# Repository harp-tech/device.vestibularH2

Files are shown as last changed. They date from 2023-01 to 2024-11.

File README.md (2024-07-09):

## Harp VestibularH2

This repository contains the device metadata, firmware and high-level interface to the VestibularH2 device. Below are simple getting started instructions for maintainers to create a new device using the automatic code generators.

### Device metadata

#### Prerequisites

1. Install [Visual Studio Code](https://code.visualstudio.com/)
2. Install the [YAML](https://marketplace.visualstudio.com/items?itemName=redhat.vscode-yaml) extension.

The `device.yml` file in the root of the project contains the VestibularH2 device metadata. A complete specification of device registers, including any bit masks, group masks, and payload specs needs to be provided for code generation to work.

### Generating interface and firmware

#### Prerequisites

1. Install [`dotnet`](https://dotnet.microsoft.com/)
2. Install `dotnet-t4`
```
dotnet tool install -g dotnet-t4
```

The `Generators` folder contains all text templates and project files required to generate both the firmware headers and the interface for the VestibularH2 device. To run the text templating engine just build the project inside this folder.

```
cd Generators
dotnet build
```

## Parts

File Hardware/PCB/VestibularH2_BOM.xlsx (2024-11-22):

VestibularVR H2-module v1.1
.on board
Qty | Parts | Value | OEPS | MPN | Device | Package | Description
21 | C1, C3, C5, C7, C9, C12, C14, C16, C17, C18, C25, C26, C27, C19, C20, C21, C22, C28, C29, C30, C31 | 100nF | OEPS010004 | C1005X7R1H104K050BB | C-EUC0402K | C0402K | CAPACITOR, European symbol
1 | R5 | 10R | OEPS020041 | ERJ-PA2J100X | R-US_R0402 | R0402 | RESISTOR, American symbol
12 | R2, R6, R8, R10, R11, R12, R13, R14, R17, R18, R19, R34 | 10k | OEPS020030 | CRCW040210K0FKED | R-US_R0402 | R0402 | RESISTOR, American symbol
1 | R21 | 15k | OEPS020015 | ERJ-2RKF1502X | R-EU_R0402 | R0402 | RESISTOR, European symbol
2 | C41, C42 | 15nF 5% | OEPS010023 | CGA2B3X7R1V153K050BB | C-EUC0402K | C0402K | CAPACITOR, European symbol
1 | R3 | 1M | OEPS020026 | CRCW04021M00FKED | R-US_R0402 | R0402 | RESISTOR, American symbol
1 | X3 | 1x2 case | OEPS070020 | 282834-2 | 22-23-2021 | 22-23-2021 | .100 (2.54mm) Center Header - 2 Pin"
2 | X4, X10 | 1x3 case | OEPS070035 | 282834-3 | 22-23-2031 | 22-23-2031 | .100 (2.54mm) Center Header - 3 Pin"
1 | X1 | 1x5 MAIN PLUG | OEPS070037 | 20.155MH/5-E | 90G-5 | 90G-5 | WEIDMUELLER CLAMP CONNECTOR
3 | X2, X5, X9 | 1x5 case | OEPS070041 | 282834-5 | 22-23-2051 | 22-23-2051 | .100 (2.54mm) Center Header - 5 Pin"
1 | R20 | 24k | OEPS020048 | ERJ-2RKF2402X | R-EU_R0402 | R0402 | RESISTOR, European symbol
1 | R1 | 330R | OEPS020037 | RC0402FR-07330RL | R-US_R0402 | R0402 | RESISTOR, American symbol
1 | C2 | 4.7nF | OEPS010001 | CC0402KRX7R8BB472 | C-EUC0402K | C0402K | CAPACITOR, European symbol
5 | C8, C10, C11, C23, C24 | 4.7uF | OEPS010018 | C1608X6S1C475K080AC | C-EUC0603K | C0603K | CAPACITOR, European symbol
3 | L1, L2, L3 | 40R@100MHz | OEPS040003 | MI0805K400R-10 | R-EU_R0805 | R0805 | RESISTOR, European symbol
3 | C4, C6, C13 | 47pF | OEPS010011 | 04025A470JAT2A | C-EUC0402K | C0402K | CAPACITOR, European symbol
1 | IC8 | ATXMEGA32A4U | OEPS080012 | ATXMEGA32A4U-AUR | XMEGA-A4_AT-XMEGA-XXA4-AUTQFP44 | TQFP44 | ATxMega a4 Serie
1 | X8 | CLCK_JACK | OEPS070025 | 35RASMT2BHNTRX | STEREO_JACK | 35RASMT2BHNTRX | CONN JACK STEREO 3.5MM SMD R/A
1 | X7 | DC_JACK2.1MM | OEPS070026 | 163-179PH-EX | DC_JACK2.1MM | DC_POWER_INPUT_2.1MM | DC Power Connectors PCB 2.1MM
1 | C15 | DNI | DNI | DNI | C-EUC0603K | C0603K | CAPACITOR, European symbol
3 | R4, R7, R9 | DNI | DNI | DNI | R-US_R0402 | R0402 | RESISTOR, American symbol
1 | IC1 | FT232RL | OEPS080013 | FT232RL | FT232RL | SSOP28 | UART/FIFO IC
1 | STATE | GREEN_LED | OEPS030005 | LTST-C191KGKT | LEDCHIP-LED0603 | CHIP-LED0603
2 | IC3, IC9 | LP5907MFX-3.3 | OEPS080016 | LP5907MFX-3.3/NOPB | TLV700XX | TSOT23-5 | C REG LINEAR 3.3V 200MA SOT23-5
12 | IC2, IC4, IC5, IC6, IC11, IC12, IC13, IC14, IC15, C16, IC17, IC18 | M74VHC1GT126DT1G | OEPS080017 | M74VHC1GT126DT1G | M74VHC1GT126DT1G | TSOP-5
1 | OSC1 | OSCILLATOR | OEPS080018 | DSC1001CI5-032.0000 | OSCILLATOR | OSCILLATOR_3.2X2.5 | XTAL OSC TCXO 32.0000MHZ HCMOS
1 | SV2 | PINHD-2X3 | OEPS070015 | 609-3210-ND | PINHD-2X3 | 2X03 | PIN HEADER
1 | IC10 | THS4281DBVT | OEPS080038 | THS4281DBVT | OPA365 | SOT23-5
1 | IC7 | USBLC6-2SC6 | OEPS030010 | USBLC6-2SC6 | USBLC6-2SC6 | SOT23-6L | TVS DIODE 5.25VWM 17VC SOT23-6
1 | X6 | USB_MINI_B | OEPS070021 | UX60-MB-5S8 | USB_MINI_B | 240-0002-1 | CONN RCPT USB2.0 MINI B SMD R/A
.off board
N.A.

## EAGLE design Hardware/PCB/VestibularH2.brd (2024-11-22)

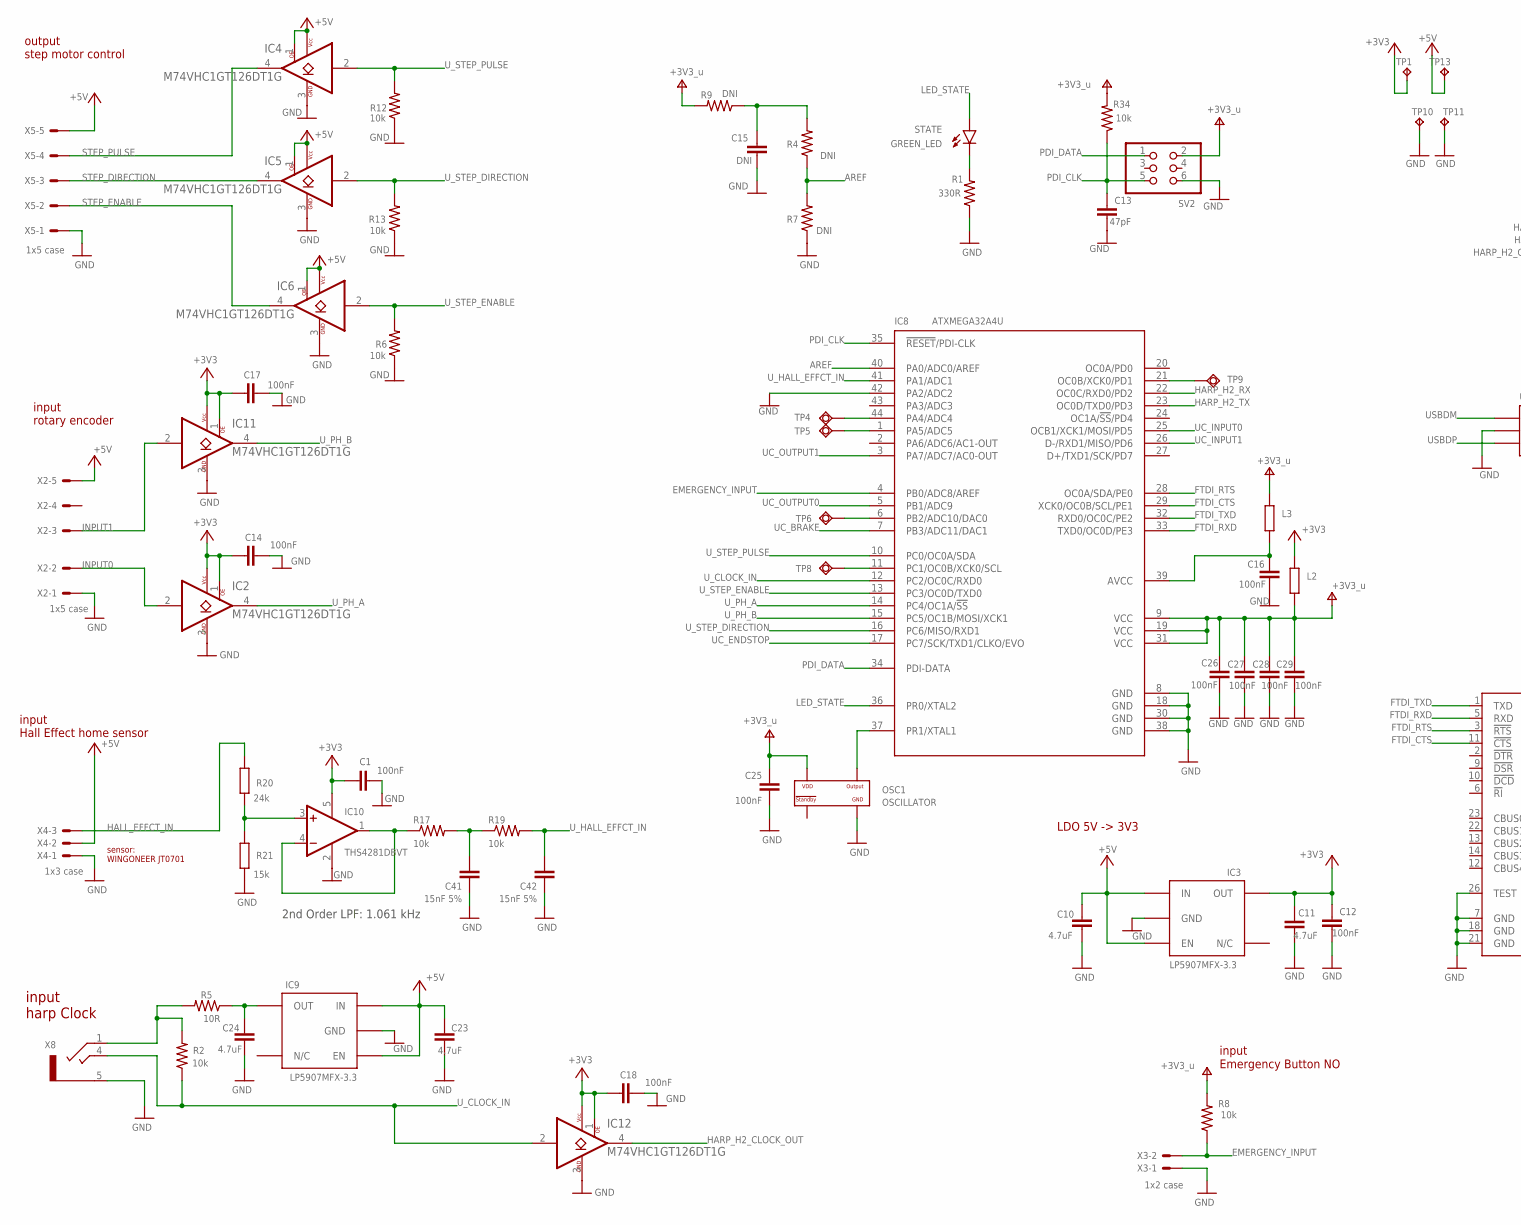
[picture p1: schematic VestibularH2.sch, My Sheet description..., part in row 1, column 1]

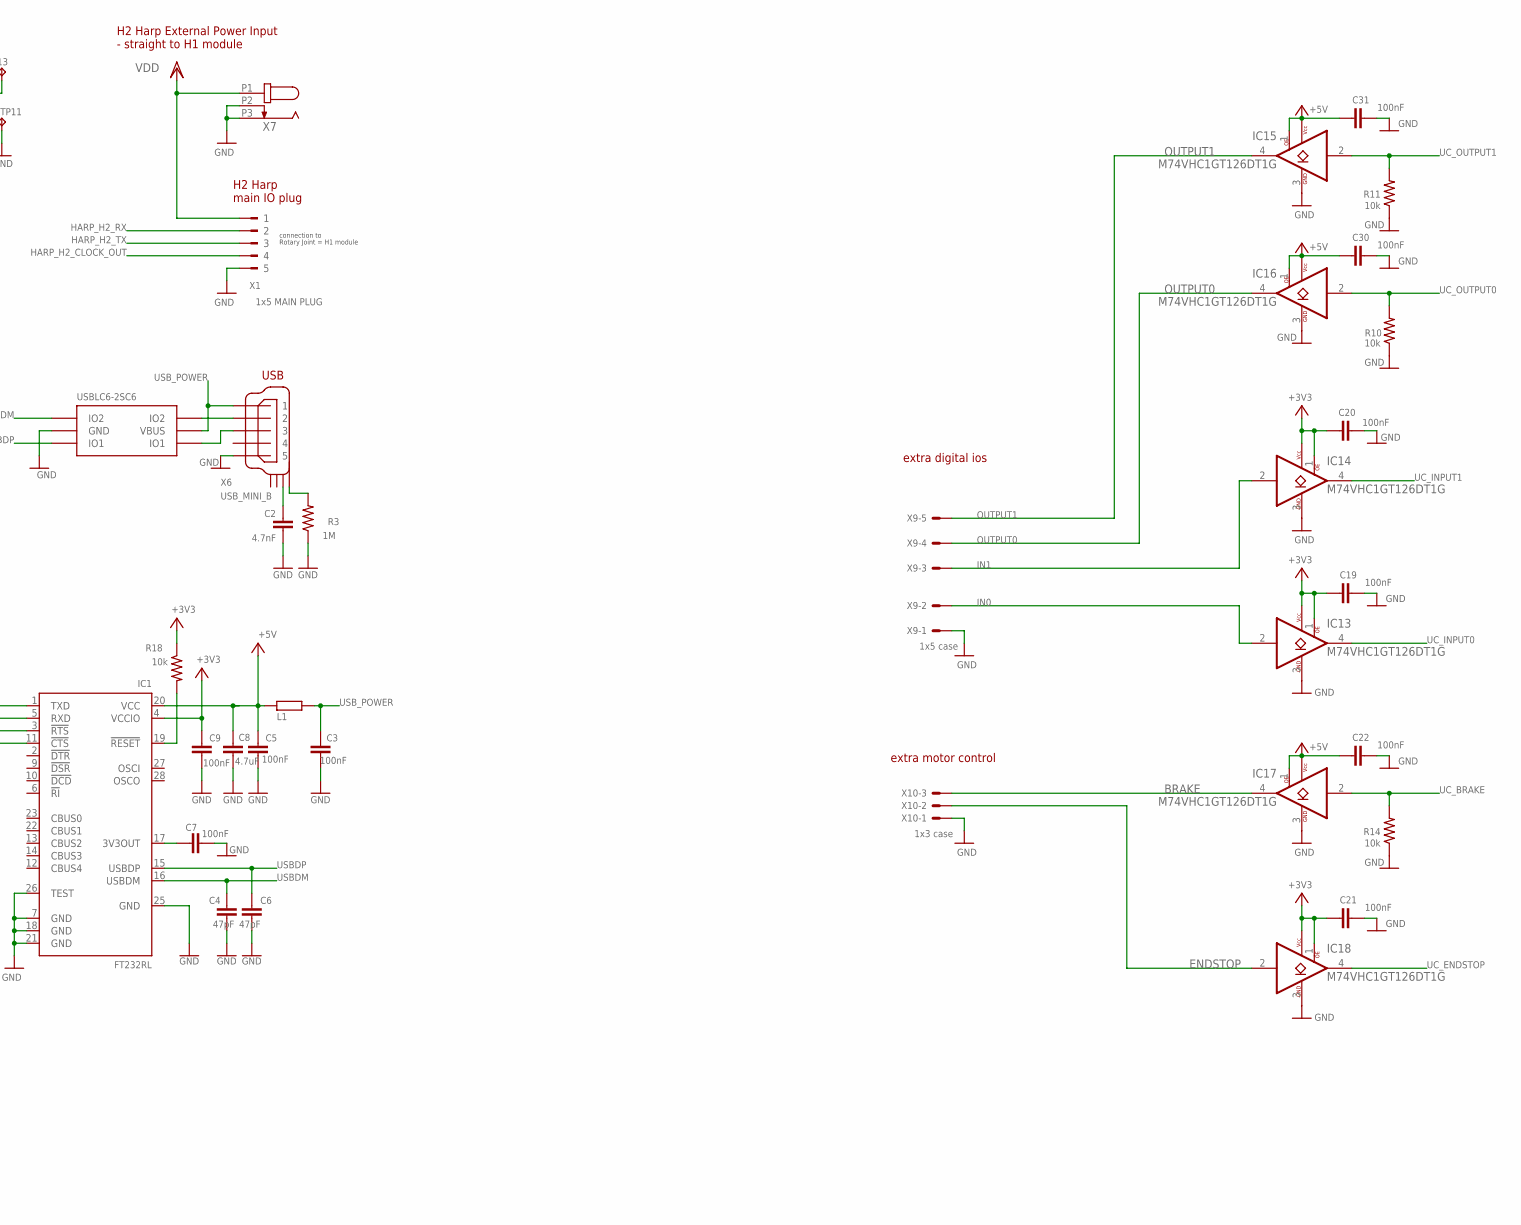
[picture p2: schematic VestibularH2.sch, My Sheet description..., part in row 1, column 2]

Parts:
C1, C3, C5, C7, C9, C12, C14, C16, C17, C18, C19, C20, C21, C22, C25, C26, C27, C28, C29, C30, C31: 100nF; C0402K; MPN C1005X7R1H104K050BB
C2: 4.7nF; C0402K; MPN CC0402KRX7R8BB472
C4, C6, C13: 47pF; C0402K; MPN 04025A470JAT2A
C8, C10, C11, C23, C24: 4.7uF; C0603K; MPN C1608X6S1C475K080AC
C15: DNI; C0603K; MPN DNI
C41, C42: 15nF 5%; C0402K; MPN CGA2B3X7R1V153K050BB
IC1: FT232RL; SSOP28; MPN FT232RL
IC2, IC4, IC5, IC6, IC11, IC12, IC13, IC14, IC15, IC16, IC17, IC18: M74VHC1GT126DT1G; TSOP-5; MPN M74VHC1GT126DT1G; DIGIKEY_PN M74VHC1GT126DT1GOSDKR-ND
IC3, IC9: LP5907MFX-3.3; TSOT23-5; MPN LP5907MFX-3.3/NOPB
IC7: USBLC6-2SC6; SOT23-6L; MPN USBLC6-2SC6
IC8: ATXMEGA32A4U; TQFP44; MPN ATXMEGA32A4U-AUR
IC10: THS4281DBVT; SOT23-5; MPN THS4281DBVT
L1, L2, L3: 40R@100MHz; R0805; MPN MI0805K400R-10
OSC1: OSCILLATOR; OSCILLATOR_3.2X2.5; MPN DSC1001CI5-032.0000
R1: 330R; R0402; MPN RC0402FR-07330RL
R2, R6, R8, R10, R11, R12, R13, R14, R17, R18, R19, R34: 10k; R0402; MPN CRCW040210K0FKED
R3: 1M; R0402; MPN CRCW04021M00FKED
R4, R7, R9: DNI; R0402; MPN DNI
R5: 10R; R0402; MPN ERJ-PA2J100X
R20: 24k; R0402; MPN ERJ-2RKF2402X
R21: 15k; R0402; MPN ERJ-2RKF1502X
STATE: GREEN_LED; CHIP-LED0603; MPN LTST-C191KGKT
SV2: PINHD-2X3; 2X03; MPN 609-3210-ND
TP1, TP10, TP11, TP13: NO_COMPONENT; B1,27
TP4, TP5, TP6, TP8, TP9: NO_COMPONENT; TP11R
X1: 1x5 MAIN PLUG; 90G-5; MPN 20.155MH/5-E
X2, X5, X9: 1x5 case; 22-23-2051; MPN 282834-5
X3: 1x2 case; 22-23-2021; MPN 282834-2
X4, X10: 1x3 case; 22-23-2031; MPN 282834-3
X6: USB_MINI_B; 240-0002-1; MPN UX60-MB-5S8
X7: DC_JACK2.1MM; DC_POWER_INPUT_2.1MM; MPN 163-179PH-EX
X8: CLCK_JACK; 35RASMT2BHNTRX; MPN 35RASMT2BHNTRX

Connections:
+3V3: C1.1, C9.1, C11.1, C12.1, C14.1, C17.1, C18.1, C19.1, C20.1, C21.1, IC1.4 (VCCIO), IC2.1 (OE), IC2.5 (VCC), IC3.5 (OUT), IC10.5 (V+), IC11.1 (OE), IC11.5 (VCC), IC12.1 (OE), IC12.5 (VCC), IC13.1 (OE), IC13.5 (VCC), IC14.1 (OE), IC14.5 (VCC), IC18.1 (OE), IC18.5 (VCC), L2.2, R18.1, TP1.TP
+5V: C5.1, C8.1, C10.1, C22.1, C23.1, C30.1, C31.1, IC1.20 (VCC), IC3.1 (IN), IC3.3 (EN), IC4.1 (OE), IC4.5 (VCC), IC5.1 (OE), IC5.5 (VCC), IC6.1 (OE), IC6.5 (VCC), IC9.1 (IN), IC9.3 (EN), IC15.1 (OE), IC15.5 (VCC), IC16.1 (OE), IC16.5 (VCC), IC17.1 (OE), IC17.5 (VCC), L1.1, TP13.TP, X2.5, X4.2, X5.5
AREF: IC8.40 (PA0/ADC0/AREF), R4.1, R7.2
BRAKE: IC17.4 (Y), X10.3
EMERGENCY_INPUT: IC8.4 (PB0/ADC8/AREF), R8.1, X3.2
ENDSTOP: IC18.2 (A), X10.2
FTDI_CTS: IC1.11 (!CTS), IC8.29 (XCK0/OC0B/SCL/PE1)
FTDI_RTS: IC1.3 (!RTS), IC8.28 (OC0A/SDA/PE0)
FTDI_RXD: IC1.5 (RXD), IC8.33 (TXD0/OC0D/PE3)
FTDI_TXD: IC1.1 (TXD), IC8.32 (RXD0/OC0C/PE2)
GND: C1.2, C2.2, C3.2, C4.2, C5.2, C6.2, C7.2, C8.2, C9.2, C10.2, C11.2, C12.2, C13.2, C14.2, C15.2, C16.2, C17.2, C18.2, C19.2, C20.2, C21.2, C22.2, C23.2, C24.2, C25.2, C26.2, C27.2, C28.2, C29.2, C30.2, C31.2, C41.1, C42.1, IC1.7 (GND), IC1.18 (GND), IC1.21 (GND), IC1.25 (GND), IC1.26 (TEST), IC2.3 (GND), IC3.2 (GND), IC4.3 (GND), IC5.3 (GND), IC6.3 (GND), IC7.P$2 (GND), IC8.8 (GND), IC8.18 (GND), IC8.30 (GND), IC8.38 (GND), IC8.42 (PA2/ADC2), IC9.2 (GND), IC10.2 (V-), IC11.3 (GND), IC12.3 (GND), IC13.3 (GND), IC14.3 (GND), IC15.3 (GND), IC16.3 (GND), IC17.3 (GND), IC18.3 (GND), OSC1.P$2 (GND), R1.1, R3.1, R6.1, R7.1, R10.1, R11.1, R12.1, R13.1, R14.1, R21.1, SV2.6, TP10.TP, TP11.TP, X1.5, X2.1, X3.1, X4.1, X5.1, X6.P$5 (5), X7.P2 (2), X7.P3 (3), X8.5, X9.1, X10.1
HALL_EFFCT_IN: R20.2, X4.3
HARP_H2_CLOCK_OUT: IC12.4 (Y), X1.4
HARP_H2_RX: IC8.22 (OC0C/RXD0/PD2), X1.2
HARP_H2_TX: IC8.23 (OC0D/TXD0/PD3), X1.3
IN0: IC13.2 (A), X9.2
IN1: IC14.2 (A), X9.3
INPUT0: IC2.2 (A), X2.2
INPUT1: IC11.2 (A), X2.3
LED_STATE: IC8.36 (PR0/XTAL2), STATE.A
unnamed: R3.2, X6.SHIELD_4
unnamed: IC7.P$4 (IO2), X6.P$2 (2)
unnamed: IC7.P$6 (IO1), X6.P$3 (3)
unnamed: R1.2, STATE.C
unnamed: IC8.44 (PA4/ADC4), TP4.TP
unnamed: IC8.1 (PA5/ADC5), TP5.TP
unnamed: IC8.6 (PB2/ADC10/DAC0), TP6.TP
unnamed: C2.1, X6.SHIELD_3
unnamed: IC8.11 (PC1/OC0B/XCK0/SCL), TP8.TP
unnamed: IC8.21 (OC0B/XCK0/PD1), TP9.TP
unnamed: C7.1, IC1.17 (3V3OUT)
unnamed: C41.2, R17.2, R19.1
unnamed: C15.1, R4.2, R9.1
unnamed: C16.1, IC8.39 (AVCC), L3.1
unnamed: IC10.1 (OUT), IC10.4 (-IN), R17.1
unnamed: IC10.3 (+IN), R20.1, R21.2
unnamed: R2.2, R5.2, X8.1
unnamed: C24.1, IC9.5 (OUT), R5.1
unnamed: IC1.19 (!RESET), R18.2
OSC2: IC8.37 (PR1/XTAL1), OSC1.P$3 (OUTPUT)
OUTPUT0: IC16.4 (Y), X9.4
OUTPUT1: IC15.4 (Y), X9.5
PDI_CLK: C13.1, IC8.35 (!RESET!/PDI-CLK), R34.1, SV2.5
PDI_DATA: IC8.34 (PDI-DATA), SV2.1
STEP_DIRECTION: IC5.4 (Y), X5.3
STEP_ENABLE: IC6.4 (Y), X5.2
STEP_PULSE: IC4.4 (Y), X5.4
UC_BRAKE: IC8.7 (PB3/ADC11/DAC1), IC17.2 (A), R14.2
UC_ENDSTOP: IC8.17 (PC7/SCK/TXD1/CLKO/EVO), IC18.4 (Y)
UC_INPUT0: IC8.25 (OCB1/XCK1/MOSI/PD5), IC13.4 (Y)
UC_INPUT1: IC8.26 (D-/RXD1/MISO/PD6), IC14.4 (Y)
UC_OUTPUT0: IC8.5 (PB1/ADC9), IC16.2 (A), R10.2
UC_OUTPUT1: IC8.3 (PA7/ADC7/AC0-OUT), IC15.2 (A), R11.2
USBDM: C4.1, IC1.16 (USBDM), IC7.P$3 (IO2)
USBDP: C6.1, IC1.15 (USBDP), IC7.P$1 (IO1)
USB_POWER: C3.1, IC7.P$5 (VBUS), L1.2, X6.P$1 (1)
U_CLOCK_IN: IC8.12 (PC2/OC0C/RXD0), IC12.2 (A), R2.1, X8.4
U_HALL_EFFCT_IN: C42.2, IC8.41 (PA1/ADC1), R19.2
U_PH_A: IC2.4 (Y), IC8.14 (PC4/OC1A/!SS)
U_PH_B: IC8.15 (PC5/OC1B/MOSI/XCK1), IC11.4 (Y)
U_STEP_DIRECTION: IC5.2 (A), IC8.16 (PC6/MISO/RXD1), R13.2
U_STEP_ENABLE: IC6.2 (A), IC8.13 (PC3/OC0D/TXD0), R6.2
U_STEP_PULSE: IC4.2 (A), IC8.10 (PC0/OC0A/SDA), R12.2
V+: C25.1, C26.1, C27.1, C28.1, C29.1, IC8.9 (VCC), IC8.19 (VCC), IC8.31 (VCC), L2.1, L3.2, OSC1.P$4 (VDD), R8.2, R9.2, R34.2, SV2.2
VDD: X1.1, X7.P1 (1)

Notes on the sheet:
H2 Harp main IO plug
input rotary encoder
input Hall Effect home sensor
input harp Clock
output step motor control
input Emergency Button NO
USB
sensor: WINGONEER JT0701
H2 Harp External Power Input - straight to H1 module
connection to Rotary Joint = H1 module
2nd Order LPF: 1.061 kHz
LDO 5V -> 3V3
extra digital ios
extra motor control

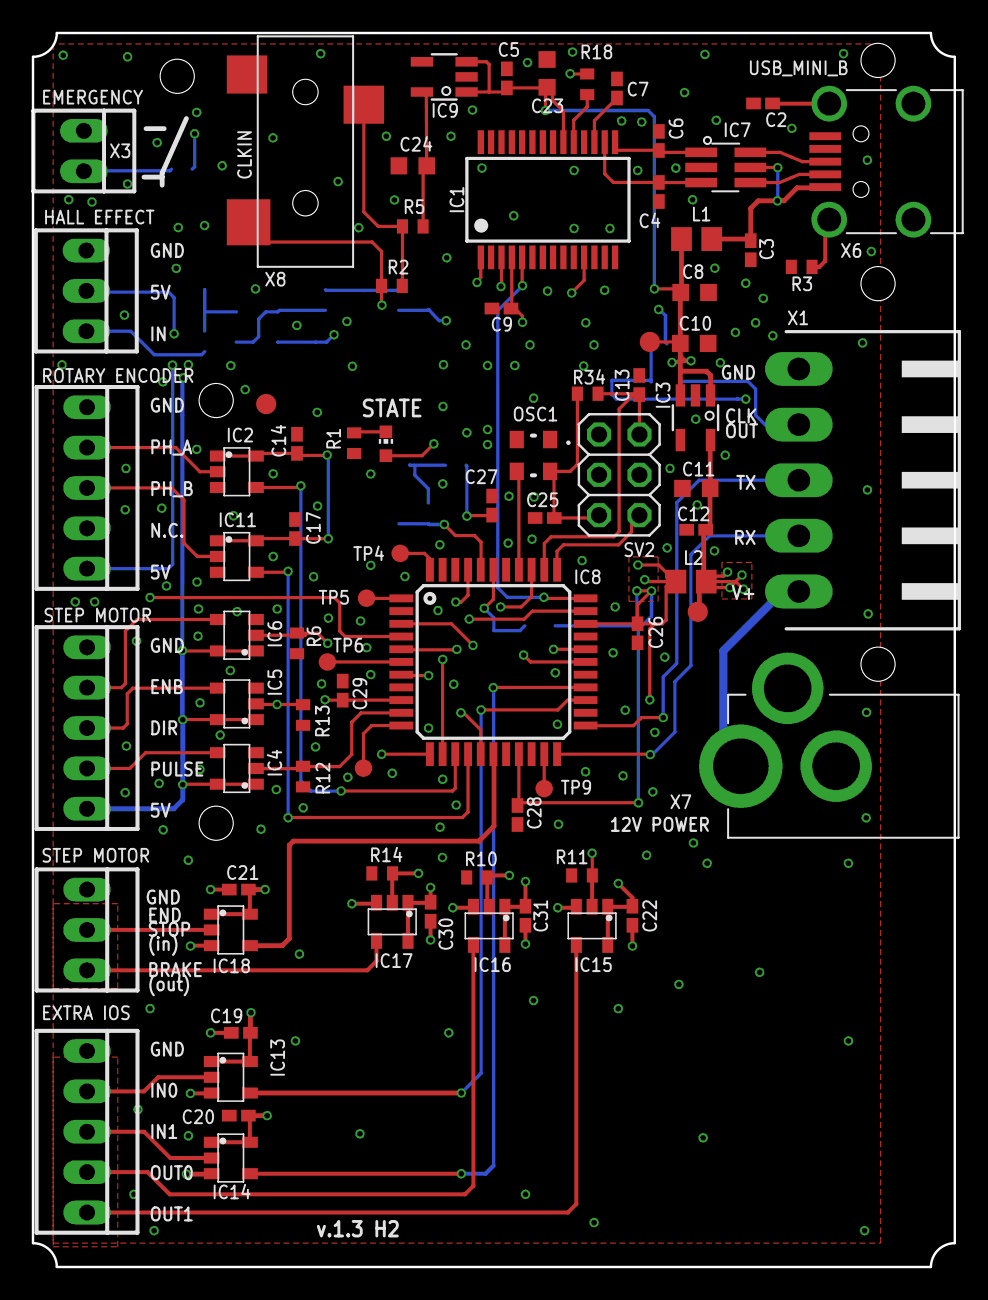
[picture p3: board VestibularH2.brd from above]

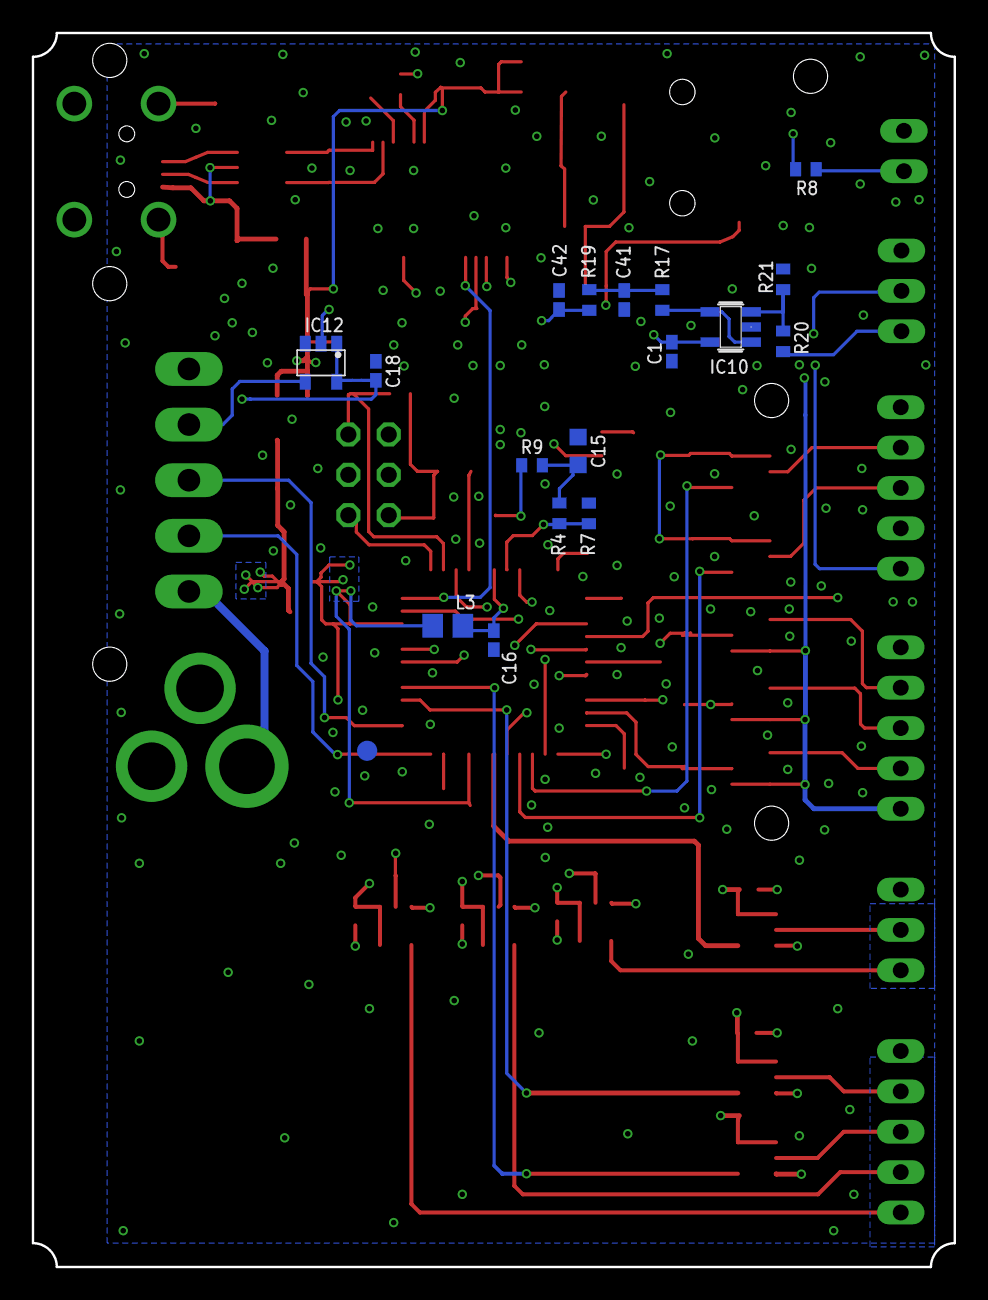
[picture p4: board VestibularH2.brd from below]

Board: 4 copper layers, 58.0 x 77.6 mm, 96 parts (18 on the bottom side), 65 nets.

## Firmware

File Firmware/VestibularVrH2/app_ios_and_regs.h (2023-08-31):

#ifndef _APP_IOS_AND_REGS_H_
#define _APP_IOS_AND_REGS_H_
#include "cpu.h"

void init_ios(void);
/************************************************************************/
/* Definition of input pins                                             */
/************************************************************************/
// STOP_SWITCH            Description: Emergency stop indication

#define read_STOP_SWITCH read_io(PORTB, 0)      // STOP_SWITCH

/************************************************************************/
/* Definition of output pins                                            */
/************************************************************************/
// MOTOR_ENABLE           Description: Enable the motor external driver
// MOTOR_PULSE            Description: Moves one step
// MOTOR_DIRECTION        Description: Sets the motor direction

/* MOTOR_ENABLE */
#define set_MOTOR_ENABLE clear_io(PORTC, 3)
#define clr_MOTOR_ENABLE set_io(PORTC, 3)
#define tgl_MOTOR_ENABLE toggle_io(PORTC, 3)
#define read_MOTOR_ENABLE read_io(PORTC, 3)

/* MOTOR_PULSE */
#define set_MOTOR_PULSE clear_io(PORTC, 0)
#define clr_MOTOR_PULSE set_io(PORTC, 0)
#define tgl_MOTOR_PULSE toggle_io(PORTC, 0)
#define read_MOTOR_PULSE read_io(PORTC, 0)

/* MOTOR_DIRECTION */
#define set_MOTOR_DIRECTION clear_io(PORTC, 6)
#define clr_MOTOR_DIRECTION set_io(PORTC, 6)
#define tgl_MOTOR_DIRECTION toggle_io(PORTC, 6)
#define read_MOTOR_DIRECTION read_io(PORTC, 6)


/************************************************************************/
/* Registers' structure                                                 */
/************************************************************************/
typedef struct
{
	uint8_t REG_CONTROL;
	int32_t REG_PULSES;
	uint16_t REG_NOMINAL_PULSE_INTERVAL;
	uint16_t REG_INITIAL_PULSE_INTERVAL;
	uint16_t REG_PULSE_STEP_INTERVAL;
	uint16_t REG_PULSE_PERIOD;
	int16_t REG_ENCODER;
	int16_t REG_ANALOG_INPUT;
	uint8_t REG_STOP_SWITCH;
	uint8_t REG_MOVING;
	int16_t REG_IMMEDIATE_PULSES;
} AppRegs;

/************************************************************************/
/* Registers' address                                                   */
/************************************************************************/
/* Registers */
#define ADD_REG_CONTROL                     32 // U8     Controls the device's modules.
#define ADD_REG_PULSES                      33 // I32    Sends the number of pulses written in this register and set the direction according to the number's signal.
#define ADD_REG_NOMINAL_PULSE_INTERVAL      34 // U16    Sets the motor's pulse interval when running at nominal speed.
#define ADD_REG_INITIAL_PULSE_INTERVAL      35 // U16    Sets the motor's maximum pulse interval, used as the first and last pulse interval of a rotation.
#define ADD_REG_PULSE_STEP_INTERVAL         36 // U16    Sets the acceleration. The pulse's interval is decreased by this value when accelerating and increased when de-accelerating.
#define ADD_REG_PULSE_PERIOD                37 // U16    Sets the period of the pulse.
#define ADD_REG_ENCODER                     38 // I16    Contains the reading of the quadrature encoder.
#define ADD_REG_ANALOG_INPUT                39 // I16    Contains the reading of the analog input.
#define ADD_REG_STOP_SWITCH                 40 // U8     Contains the state of the stop switch.
#define ADD_REG_MOVING                      41 // U8     Contains the state of the motor.
#define ADD_REG_IMMEDIATE_PULSES            42 // I16    Sets immediately the motor's pulse interval. The value's signal defines the direction.

/************************************************************************/
/* PWM Generator registers' memory limits                               */
/*                                                                      */
/* DON'T change the APP_REGS_ADD_MIN value !!!                          */
/* DON'T change these names !!!                                         */
/************************************************************************/
/* Memory limits */
#define APP_REGS_ADD_MIN                    0x20
#define APP_REGS_ADD_MAX                    0x2A
#define APP_NBYTES_OF_REG_BANK              21

/************************************************************************/
/* Registers' bits                                                      */
/************************************************************************/
#define B_ENABLE_MOTOR                     (1<<0)       // 
#define B_DISABLE_MOTOR                    (1<<1)       // 
#define B_ENABLE_ANALOG_IN                 (1<<2)       // 
#define B_DISABLE_ANALOG_IN                (1<<3)       // 
#define B_ENABLE_QUAD_ENCODER              (1<<4)       // 
#define B_DISABLE_QUAD_ENCODER             (1<<5)       // 
#define B_RESET_QUAD_ENCODER               (1<<6)       // 
#define B_STOP_SWITCH                      (1<<0)       // 
#define B_IS_MOVING                        (1<<0)       // 

#endif /* _APP_REGS_H_ */

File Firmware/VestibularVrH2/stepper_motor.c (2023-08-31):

#include "stepper_motor.h"
#include "app_ios_and_regs.h"

/************************************************************************/
/* Global Parameters                                                    */
/************************************************************************/
extern AppRegs app_regs;

uint16_t m_pulse_period_us;
uint16_t m_min_pulse_interval_us;
uint16_t m_max_pulse_interval_us;
uint16_t m_pulse_step_interval_us;

int16_t ramp_steps;

/************************************************************************/
/* Update Global Parameters                                             */
/************************************************************************/

void update_nominal_pulse_interval (uint16_t time_us)
{
	m_min_pulse_interval_us = time_us >> 1;
	
	ramp_steps = (m_max_pulse_interval_us - m_min_pulse_interval_us) / m_pulse_step_interval_us;
}

void update_initial_pulse_interval (uint16_t time_us)
{
	m_max_pulse_interval_us = time_us >> 1;
	
	ramp_steps = (m_max_pulse_interval_us - m_min_pulse_interval_us) / m_pulse_step_interval_us;
}

void update_pulse_step_interval (uint16_t time_us)
{
	m_pulse_step_interval_us = time_us >> 1;
	
	ramp_steps = (m_max_pulse_interval_us - m_min_pulse_interval_us) / m_pulse_step_interval_us;
}

void update_pulse_period (uint16_t time_us)
{
	m_pulse_period_us = time_us >> 1;
	
	ramp_steps = (m_max_pulse_interval_us - m_min_pulse_interval_us) / m_pulse_step_interval_us;
}

/************************************************************************/
/* Globals                                                              */
/************************************************************************/
uint16_t motor_target;
uint16_t remaining;

uint32_t steps_target;
uint32_t steps_count;
uint32_t steps_remaining;

bool motor_is_running = false;
bool moving_positive;
bool decreasing_speed;

/************************************************************************/
/* Functions                                                            */
/************************************************************************/
void start_rotation (int32_t requested_steps)
{
	if (requested_steps > 0)
	{
		set_MOTOR_DIRECTION;
		moving_positive = true;
		steps_target = (uint32_t)requested_steps;
	}
	else
	{
		clr_MOTOR_DIRECTION;
		moving_positive = false;
		steps_target = (uint32_t)(~requested_steps + 1);
	}	
	
	steps_count = 0;				// Reset steps counter
	steps_remaining = 0;			// Reset remaining steps
	//TCD1_CNT = 0x8000;			// Reset encoder
	
	decreasing_speed = false;	// Reset decreasing speed flag
	motor_is_running = true;	// Update global with motor state
	
	/* Start the generation of pulses */
	timer_type0_pwm(&TCC0, TIMER_PRESCALER_DIV64, m_max_pulse_interval_us, m_pulse_period_us, INT_LEVEL_MED, INT_LEVEL_MED);
}

void stop_rotation (void)
{
	timer_type0_stop(&TCC0);
	motor_is_running = false;
}

int32_t user_sent_request (int32_t requested_steps)
{
	if (!motor_is_running)
	{
		start_rotation(requested_steps);
		return 0;
	}
	else
	{
		if ((requested_steps > 0) && (moving_positive == true))
		{			
			steps_target += requested_steps;
			return 0;
		}
		
		if ((requested_steps < 0) && (moving_positive == false))
		{
			steps_target += (uint32_t)(~requested_steps + 1);
			return 0;
		}
		
		if ((requested_steps > 0) && (moving_positive == false))
		{
			if (decreasing_speed)
			{
				return requested_steps;
			}
			else if (steps_count <= ramp_steps)
			{
				return requested_steps;
			}
			else
			{
				uint32_t available_steps_to_decrease = steps_remaining - ramp_steps - 1;
				
				if (requested_steps <= available_steps_to_decrease)
				{
					steps_target -= requested_steps;
					return 0;
				}
				else
				{
					steps_target -= available_steps_to_decrease;
					return requested_steps - available_steps_to_decrease;
				}
			}
		}
		
		if ((requested_steps < 0) && (moving_positive == true))
		{
			if (decreasing_speed)
			{
				return requested_steps;
		}
		else if (steps_count <= ramp_steps)
		{
			return requested_steps;
		}
			else
			{
				uint32_t available_steps_to_decrease = steps_remaining - ramp_steps - 1;
				
				if ((~requested_steps+1) <= available_steps_to_decrease)
				{
					steps_target -= (uint32_t)(~requested_steps + 1);
					return 0;
				}
				else
				{
					steps_target -= available_steps_to_decrease;
					return requested_steps + available_steps_to_decrease;
				}
			}
		}
	}
}

ISR(TCC0_OVF_vect/*, ISR_NAKED*/)
{	
	if (TCC0_INTCTRLB == 0)
	{
		TCC0_PER = (app_regs.REG_IMMEDIATE_PULSES >> 1) - 1;
		TCC0_CCA = app_regs.REG_IMMEDIATE_PULSES >> 2;
		
		return;
	}
	
	remaining = motor_target - steps_count;
	
	
	steps_count++;
	
	steps_remaining = steps_target - steps_count; 
		
	if ((steps_remaining <= steps_count) && (steps_remaining <= ramp_steps))
	{		
		decreasing_speed = true;
		
		/* Decrease motor speed */
		if (TCC0_PER < m_max_pulse_interval_us)
		{
			TCC0_PER = (TCC0_PER + m_pulse_step_interval_us > m_max_pulse_interval_us)? m_max_pulse_interval_us : TCC0_PER + m_pulse_step_interval_us;
		}
	}
	else
	{
		decreasing_speed = false;
		
		/* Increase motor speed */
		if (TCC0_PER > m_min_pulse_interval_us)
		{
			TCC0_PER = (TCC0_PER - m_pulse_step_interval_us < m_min_pulse_interval_us)? m_min_pulse_interval_us : TCC0_PER - m_pulse_step_interval_us;
		}	
	}
}

bool send_motor_stopped_notification = false;

ISR(TCC0_CCA_vect/*, ISR_NAKED*/)
{		
	if (steps_count == steps_target)
	{
		/* Stop motor */
		stop_rotation();
		
		/* Since this is used at MID level interrupts, send an event from here can happen in the middle of other event */
		send_motor_stopped_notification = true;
	}
}

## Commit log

2022-11-22 BOMs & start Harp Motor device H2-module v1.0
    . almost final BOMs versions for VestibularVR H1-module v1.0 & Lick Sensor module v1.0
    . start of new project Harp Motor device H2-module v1.0
    [Harp Motor device H2-module v1.0.brd, Harp Motor device H2-module v1.0.sch]
2022-11-23 Harp Motor device H2 - design
    still first steps on Eagle Harp Motor device H2 design
    [Harp Motor device H2-module v1.0.brd, Harp Motor device H2-module v1.0.sch]
2022-12-05 VestibularVR H1BOM updates & Lick Sensor step on
    - VestibularVR H1
    . component ref updated
    . BOM file updated
    - Lick Sensor module v1.0
    . still only on schematic design
    [Harp Motor H2-module v1.0.brd, Harp Motor H2-module v1.0.sch, Harp Motor device H2-module v1.0.brd]
2022-12-07 Harp Motor device H2-module v1.0 - Schematic step on
    Harp Motor device H2-module v1.0 - Schematic step on
    [Harp Motor H2-module v1.0.brd, Harp Motor H2-module v1.0.sch]
2022-12-09 Harp Motor device H2-module v1.0 - design proceeding
    Harp Motor device H2-module v1.0 - design proceeding
    [Harp Motor H2-module v1.0.brd, Harp Motor H2-module v1.0.sch]
2022-12-13 Harp Motor device H2-module v1.0 - 1st 'finished' version
    Harp Motor device H2-module v1.0 - 1st 'finished' version
    - missing:
    . some schm & pcb review with Filipe
    . components order codes & BOM
    [Harp Motor H2-module v1.0.brd, Harp Motor H2-module v1.0.sch]
2022-12-14 Harp Motor device H2-module v1.0; commit after revision
    Harp Motor device H2-module v1.0:
    - commit after revisions made with Filipe @Dezember 14th 2022
    - missing components OEPS code & BOM
    [Harp Motor H2-module v1.0.brd, Harp Motor H2-module v1.0.sch]
2022-12-16 Harp Motor device H2-module v1.0 - last revision with Filipe
    - extra R0 on some stages
    - IO headers - GND pin was on wrong end
    - rebuild user-friend labelling
    - still missing OEPS components code & BOM
    [Harp Motor H2-module v1.0.brd, Harp Motor H2-module v1.0.sch]
2022-12-16 Harp Motor device H2-module v1.0 - silk screen corrections
    Harp Motor device H2-module v1.0
    - silk screen positions corrections
    - still missing OEPS parts codes & BOM
    [Harp Motor H2-module v1.0.brd]
2022-12-19 Harp Motor device H2-module v1.0 - final changes
    Harp Motor device H2-module v1.0 - final PCB changes
    - labels sizes & positions modified
    - removed clock conn from micro to main plug; added direct buffer from clock_in to main harp plug;
    - corrected Harp_Tx & Harp_Rx pins
    - still missing BOM & OEPS components codes
    [Harp Motor H2-module v1.0.brd, Harp Motor H2-module v1.0.sch]
2022-12-20 Harp Motor device H2-module v1.0 - BOM not finished
    - BOM committed; not yet finished
    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
    [Harp Motor H2-module v1.0 BOM.xlsx, Harp Motor H2-module v1.0.brd, Harp Motor H2-module v1.0.sch]
2022-12-22 Harp Motor device H2-module v1.0 - BOM updated
    Harp Motor device H2-module v1.0 - BOM updated
    - still missing component's codes
    [Harp Motor H2-module v1.0 BOM.xlsx, Harp Motor H2-module v1.0.brd, Harp Motor H2-module v1.0.sch]
2023-01-10 Harp Motor device H2-module v1.0 BOM updated
    Harp Motor device H2-module v1.0 BOM updated
    - OEPS & MPN components code changed
    - new BOM generated
    [Harp Motor H2-module v1.0 BOM.xlsx, Harp Motor H2-module v1.0.brd, Harp Motor H2-module v1.0.sch]
2023-01-11 Harp Motor device H2-module v1.0 - BOM updated
    - new component codes on schematic
    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
    [Harp Motor H2-module v1.0 BOM.xlsx, Harp Motor H2-module v1.0.brd, Harp Motor H2-module v1.0.sch]
2023-01-12 Harp Motor device H2-module v1.0 - BOM updated
    - THS4281DBVT OPES code updated: OEPS080038
    - schematic updated
    - BOM updated
    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
    [Harp Motor H2-module v1.0 BOM.xlsx, Harp Motor H2-module v1.0.brd, Harp Motor H2-module v1.0.sch]
2023-01-15 Reorganize repository to match standard template
    [Harp Motor H2-module v1.0 BOM.xlsx, Harp Motor H2-module v1.0.brd, Harp Motor H2-module v1.0.sch]
2023-03-13 Added the first firmware files.
    [registers.xls]
2023-03-13 Added equation to calculate voltage.
2023-03-13 Cancel pulse drive when the user disables the motor.
2023-03-13 Disable medium and high level interrupts.
    Disable medium and high level interrupts to transform the motor global variables into global atomic variables.
2023-03-15 Created new register called Moving.
    Took the opportunity to correct a typo.
    [registers.xls]
2023-03-15 Implemented protection to stop motor.
    Implemented protection to stop motor when the device goes to Standby Mode.
2023-05-16 Decreased step interval to increase motor speed.
2023-05-16 Added new register IMMEDIATE_PULSES on address 42.
    [registers.xls]
2023-09-05 Replaced files with PCB version 1.1.
    [VestibularH2.brd, VestibularH2.sch]
2023-09-05 Replaced BOM to match PCB version 1.1.
    [Harp Motor H2-module v1.0 BOM.xlsx, VestibularH2_BOM.xlsx]
2023-11-27 Update device schema
2024-03-20 Fix top silk.
    Fixed label of Hall effect' connector.
    [VestibularH2.brd]
2024-06-28 Implemented serial reception.
    [registers.xls]
2024-11-18 Created the schematic with new ios.
    [VestibularH2.brd, VestibularH2.sch, VestibularH2_BOM.xlsx]
2024-11-22 Finalized the layout.
    [VestibularH2.brd, VestibularH2.sch]
